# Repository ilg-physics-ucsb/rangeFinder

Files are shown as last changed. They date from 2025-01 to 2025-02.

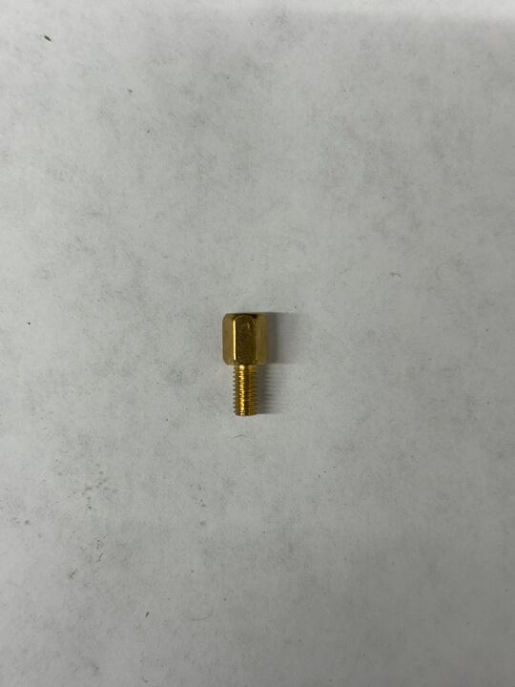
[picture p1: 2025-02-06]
Documentation/Components/M3x6mm_Standoff.jpg

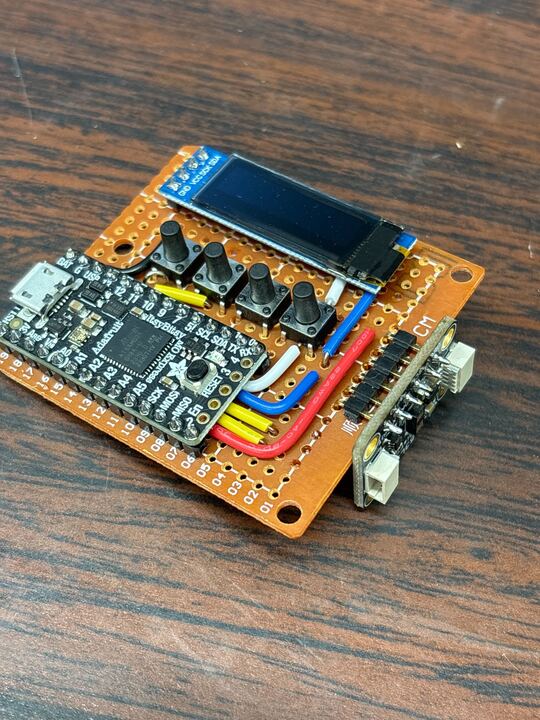
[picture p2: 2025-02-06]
Documentation/CircuitInstructions/CircuitFinished.jpg

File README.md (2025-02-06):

# Range Finder

This repository should hold everything related to the range finders made by the ILG for the 6AL lab series. These range finders were made using off the shelf components from adafruit and amazon with a 3D printed case, to solve the issue of tedious data taking in the Energy Conservation lab in 6AL. For information on the components visit the datasheets folder, for information on the housing view the CAD folder, and to view the code view the code folder. 

## Assembly Instructions

#### Materials required

* 1 [Adafruit ItsyBitsy M0](/Documentation//Components/ItsyBitsyM0ExpressGuide.pdf)
* 1 [Adafruit VL53L1X Breakout Board](/Documentation/Components/VL53L1XGuide.pdf)
* 1 [128x32 I2C SSD1306 OLED Display](/Documentation/Components/SSD1306OLEDGuide.pdf)
* 4 [6x6mm Tall Buttons with Colored Caps](/Documentation/Components/6mmx6mm_Button_Tall.jpg)
* 1 [5cm x 7cm Perf Board](/Documentation/Components/5cmx7cm_PerfBoard.jpg)
* 3 M3x6mm Screws
* 3 [M3x6mm Standoffs](/Documentation/Components/M3x6mm_Standoff.jpg)
* 3 [M3x6mm Threaded Inserts](/Documentation/Components/M3x6mm_ThreadedInsert.jpg)
* 2 [M4 Threaded Banana Plugs](/Documentation/Components/M4_BananaPlug.jpg)
* 2 [M4x8mm Threaded Inserts](/Documentation/Components/M4x8mm_ThreadedInsert.jpg)

#### Assembling the Internals

The Perf board must be cut fairly exactly to size for it to fit in the case. 

* First [score and snap](/Documentation/PerfBoardInstructions/ScoredPerfBoard.jpg) the perf board along row 20. 
* Then [sand along the edge](/Documentation/PerfBoardInstructions/SandedPerfBoard.jpg) to make smooth. 
* Lastly to attach you need [M3 clearance holes drilled](/Documentation/PerfBoardInstructions/FinishedPerfBoard.jpg) into the two holes at the bottom and into the hole at J18. 

From here you can solder all the connections together on the perf board. The schematic used is [shown here](/Documentation/CircuitInstructions/RangeFinderSchematic.pdf). The connections are tight so here are pictures of the asiest way to solder all the connections together: [Top of Circuit](/Documentation/CircuitInstructions/CircuitTop.jpg), [Bottom of Circuit](/Documentation/CircuitInstructions/CircuitBottom.jpg), and a [Finished Circuit](/Documentation/CircuitInstructions/CircuitFinished.jpg). The solder joints must be carefully checked, the ItsyBitsy has a tendency to shut down the I2C lines if there is too much noise on SCL or SDA causing the system to no longer work. If the circuit is not working you should first check that all connectons made are correct according to the scematic, and then if it still is failing ensure that all the solder joints are clean and nothing is even close to touching the SCL or SDA lines. 

#### Assembling the Case

The files for the case can be found [here](/CAD/). This folder contains the raw [Fusion 360 file](/CAD/RangeFinderCase.f3d) if it needs to be edited in the future, as well as .stl files for the [lid](/CAD/RangeFinderLid.stl) and the [main body](/CAD/RangeFinderBody.stl), for easier printing. Once the files are printed you need to [install the threaded inserts](Documentation/CaseInstructions/InstallThreadedInserts.jpg) into the holes. The 3 M3x6mm threaded inserts go in the [main cavity of the body](Documentation/CaseInstructions/M3InsertLocation.jpg) and the 2 M4x8mm threaded inserts go in the [bottom channel](Documentation/CaseInstructions/M4InsertLocation.jpg). 

From here you just put everything together. First you [screw in the M4 Banana Plugs](Documentation/CaseInstructions/M4BananaPlugInsert.jpg) to interface with the air track. Next you [screw the main circuit in](Documentation/CaseInstructions/CircuitInCase.jpg) to the case with the M3x6mm Standoffs. The last step is to just [screw on the lid](Documentation/CaseInstructions/FinalCase.jpg) with the M3x6mm screw. 

#### Flashing the Code

The code for this system was made in Arduino IDE and requires the built in libraries to fuction properly, so to flash the code you must use this IDE. The raw .ino file can be found [here](/Code/RangeFinderCode/). To properly compile the code you will also need to install the core for the ItsyBitsy through Arduino IDE, to do this you will need to follow the steps in the ItsyBitsy datasheet. The code also requires a few libraries to work, you can find all of these [here](/Code/Libraries/). You will need copy these over into the libraries sub-folder of wherever the Aduino IDE stores its files, often in "~/documents/Arduino/". From here you should be able to compile and upload the code to the ItsyBitsy when it is plugged into your computer.

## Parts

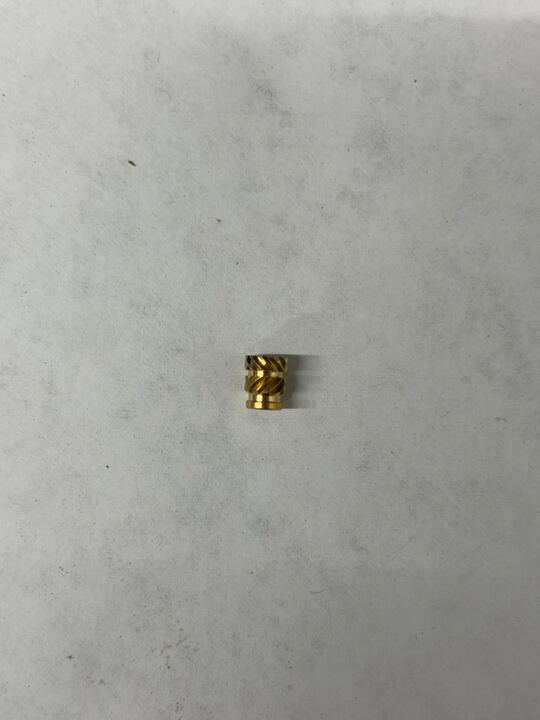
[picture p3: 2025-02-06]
Documentation/Components/M3x6mm_ThreadedInsert.jpg

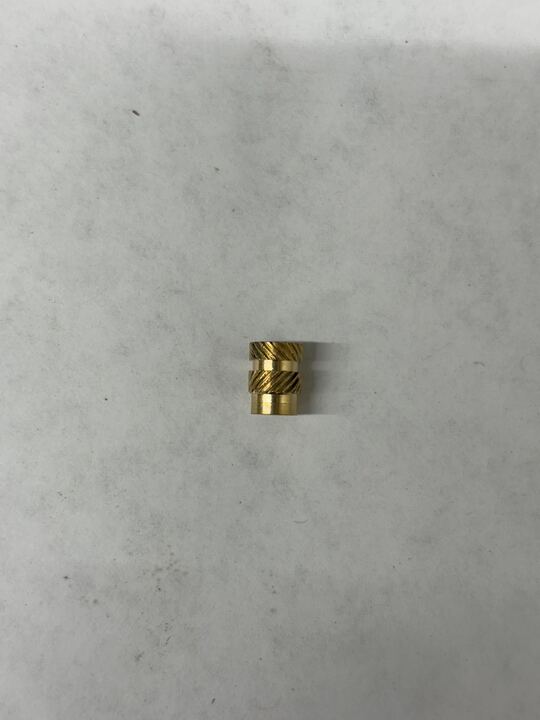
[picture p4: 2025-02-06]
Documentation/Components/M4x8mm_ThreadedInsert.jpg

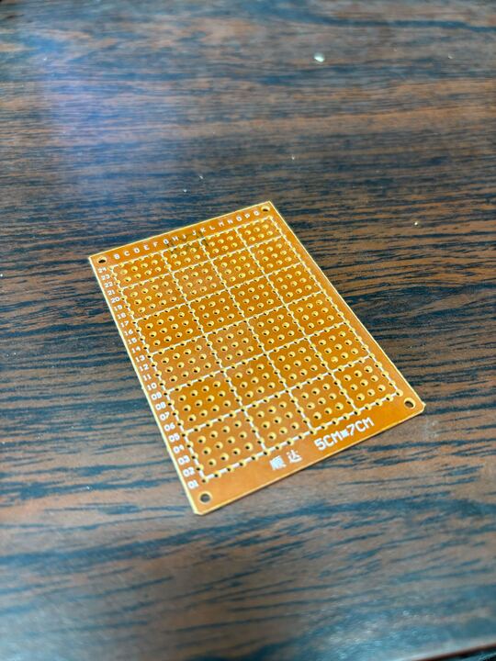
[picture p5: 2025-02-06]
Documentation/Components/5cmx7cm_PerfBoard.jpg

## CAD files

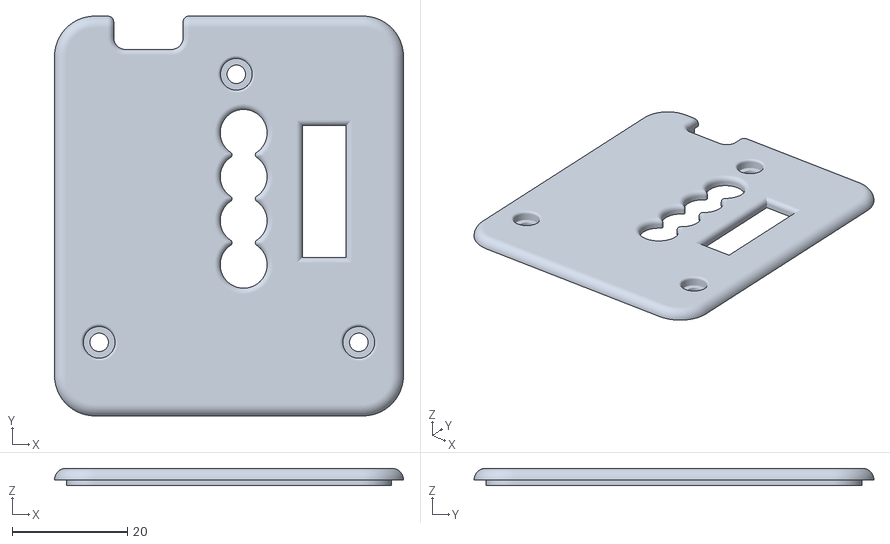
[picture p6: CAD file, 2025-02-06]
CAD/RangeFinderLid.stl
60.5 x 69.3 x 3.00

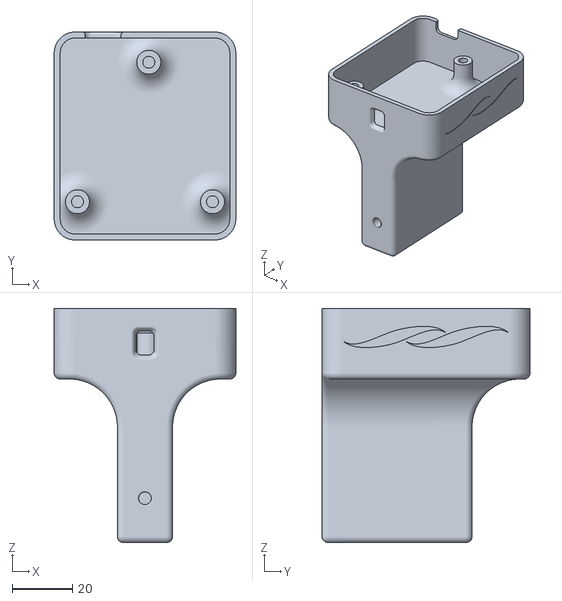
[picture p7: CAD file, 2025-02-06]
CAD/RangeFinderBody.stl
60.5 x 69.3 x 77.9

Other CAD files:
CAD/RangeFinderCase.f3d

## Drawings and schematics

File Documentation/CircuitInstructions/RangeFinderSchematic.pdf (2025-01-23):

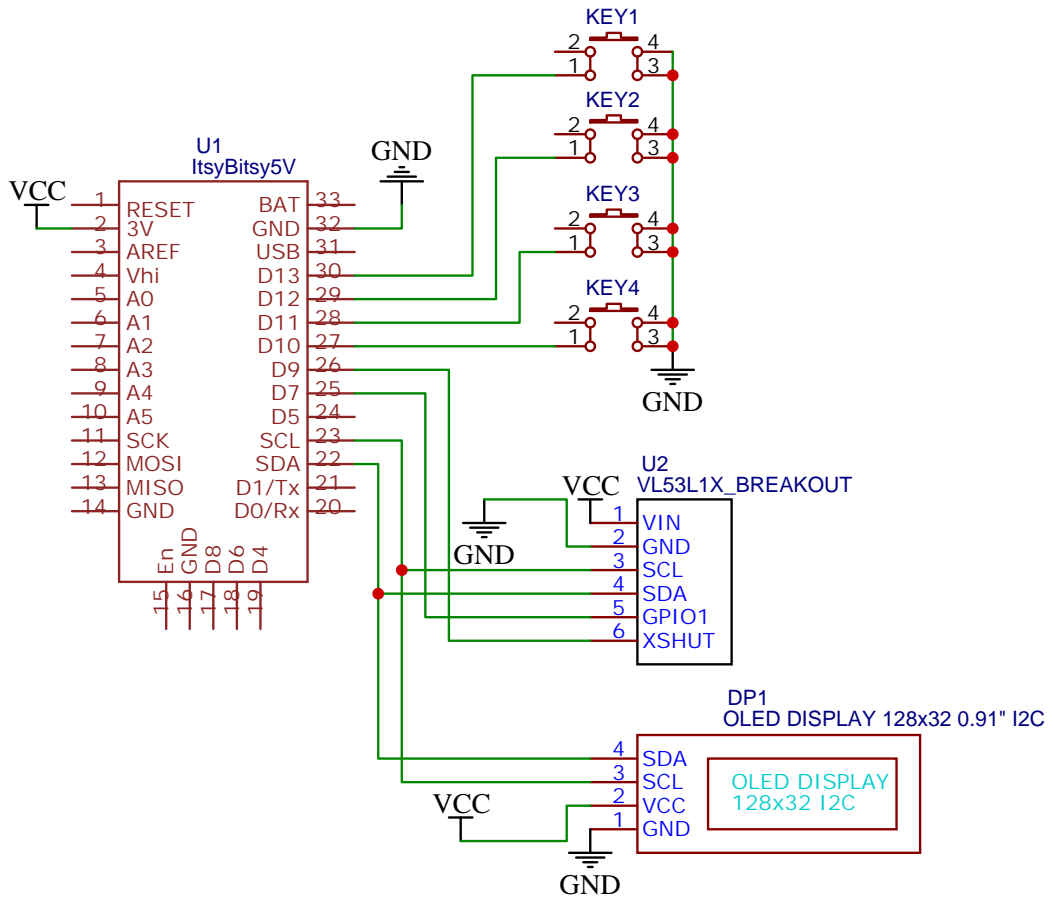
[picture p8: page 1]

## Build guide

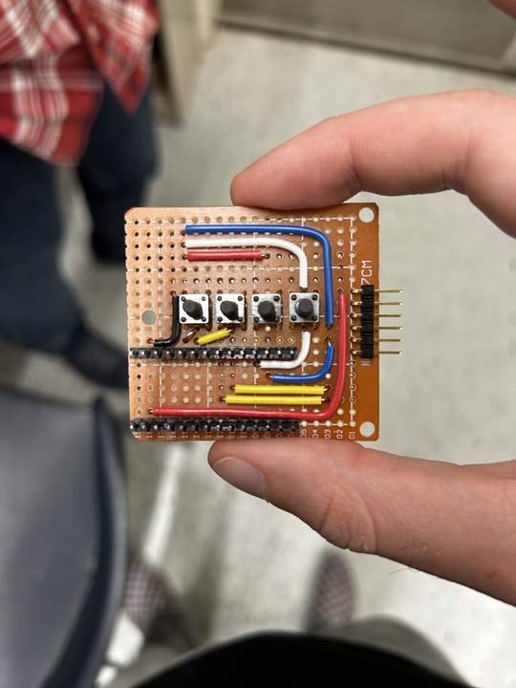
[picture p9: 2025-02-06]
Documentation/CircuitInstructions/CircuitTop.jpg

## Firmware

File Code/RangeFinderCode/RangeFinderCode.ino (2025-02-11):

#include <Adafruit_GFX.h>
#include <Adafruit_SSD1306.h>
#include <vl53l1x_class.h>
#include <Keyboard.h>
#include <Adafruit_DotStar.h>

#define SCREEN_WIDTH 128 // OLED display width, in pixels
#define SCREEN_HEIGHT 32 // OLED display height, in pixels
#define OLED_RESET     -1 // Reset pin # (or -1 if sharing Arduino reset pin)
#define SCREEN_ADDRESS 0x3C // See datasheet for Address; 0x3D for 128x64, 0x3C for 128x32

#define PIN_INDICATOR 2   // Light up LED
#define PIN_START 10      // Green Button
#define PIN_STOP 13       // Red Button
#define PIN_TIME 11       // Blue Button
#define PIN_RATE 12       // Yellow Button
#define PIN_INTERRUPT 7   // Interrupt for the Range Finder
#define PIN_SHUTDOWN 9    // Shutdown pin for the Range Finder

#define DATA_AVG_MAX 10   // How manyt samples for the rolling average

Adafruit_SSD1306 display(SCREEN_WIDTH, SCREEN_HEIGHT, &Wire, OLED_RESET);
VL53L1X rangeFinder(&Wire, PIN_SHUTDOWN);
Adafruit_DotStar onBoardLED(DOTSTAR_NUM, PIN_DOTSTAR_DATA, PIN_DOTSTAR_CLK, DOTSTAR_BRG);

uint8_t dataFlag = 0 ;
int dataStatus = 0 ;
int objectNum = 0 ;
int dataRawTime = 50 ; // Time for the sensor to average over 
uint16_t dataRaw = 0 ;
float data = 0 ;
int dataAvg[DATA_AVG_MAX] ;
unsigned long dataTime[DATA_AVG_MAX] ;
int dataAvgIndex = 0 ;

int dataRecordingIntervalIndex = 4 ;
unsigned long dataRecordingInterval[] = {10000, 15000, 20000, 30000, 5000} ; // How long to record data in millis
int dataRecordingIntervalSize = 5 ;                                          // Number of entries in the array above
unsigned long dataRecordingTimeStart = 0 ;
char dataRecordingIntervalBuff[5] ;
int dataRecordingIntervalPos[2][2] = { {94, 24}, {30, 0} } ;


int dataFilterIntervalIndex = 0 ;
unsigned long dataFilterInterval[] = {1, 2, 5, 10, 20};              // Time for the us to filter the sensors data over as number of samples
int dataFilterIntervalSize = 5 ;                                             // Number of entries in the array above
unsigned long dataFilterTime = 0 ;    
char dataFilterIntervalBuff[5] ;   
int dataFilterIntervalPos[2][2] = { {30, 24}, {94, 0} } ;

// legacy variables for filtering
float dataLast = 0 ;
float dataLastLast = 0 ;
float timeLast = 0 ;     // Last time for velocity
float timeLastLast = 0 ; // Last Last time for velocity
float posLast = 0 ;         // Last position for filtering
float velLast = 0 ;         // Last velocity for filtering
float alpha = 0.5 ;        // Factor for data smoothing 
float alphaInv = 1-alpha ;  // Precalculating 

// Data to be stored and written to computer
float time = 0 ;         // Time of recorded data
float pos = 0 ;             // Smoothed data in m
float vel = 0 ;             // Smoothed data of velocity in m/s
char posBuff[5] ;
char velBuff[6] ;
char timeBuff[6] ;

bool dataNewFlag = 0 ;
int dataArrayIndex = 0 ;
int dataArrayCounter = 0 ;
int dataArrayCounterSub = 0 ;
float timeArray[1000] ;
float posArray[1000] ;
float velArray[1000] ;
unsigned long keyboardDelay = 50 ;
unsigned long keyboardTimer = 0 ;


int posPixelX = 0 ;
int posPixelY = 0 ;
int displayRotation = 0 ;
int dataDistancePos[2][2] = { {22, 0}, {22, 16} } ;
int dataUploadPos[2][2] = { {89, 0}, {3, 0} }  ;
int dataCancelPos[2][2] = { {3, 0}, {89, 0} }  ;

unsigned long displayInterval = 200 ;
unsigned long displayTime = 0 ;

unsigned long buttonDebounceWait   = 20 ;  // In millis
unsigned long buttonStartDebounce  = 0 ;
unsigned long buttonStopDebounce   = 0 ;
unsigned long buttonRateDebounce   = 0 ;
unsigned long buttonTimeDebounce   = 0 ;
bool buttonStartToggle    = 0 ;
bool buttonStopToggle     = 0 ;
bool buttonRateToggle     = 0 ;
bool buttonTimeToggle     = 0 ;
bool buttonStartFlag      = 0 ;
bool buttonStopFlag       = 0 ;
bool buttonRateFlag       = 0 ;
bool buttonTimeFlag       = 0 ;

int state = 0 ;
int stateLast = 0 ;
bool displayFlag = 0 ;
volatile bool interruptFlag = 0;
unsigned long t0 = 0 ;


void interruptRangeFinder() {
  interruptFlag = 1;
}


// the setup function runs once when you press reset or power the board
void setup() {
  // Init on Board LED
  onBoardLED.begin(); // Initialize pins for output
  onBoardLED.setBrightness(80);
  onBoardLED.show();  // Turn all LEDs off ASAP


  // initialize GPIO pins
  pinMode(PIN_START, INPUT_PULLUP) ;
  pinMode(PIN_STOP,  INPUT_PULLUP) ;
  pinMode(PIN_TIME,  INPUT_PULLUP) ;
  pinMode(PIN_RATE,  INPUT_PULLUP) ;
  pinMode(PIN_INDICATOR,   OUTPUT) ;
  pinMode(PIN_INTERRUPT, INPUT_PULLUP);
  attachInterrupt(PIN_INTERRUPT, interruptRangeFinder, RISING) ;

  // Start up the rangefinder in interrupt mode
  Serial.println("Init Range Finder") ;
  onBoardLED.setPixelColor(0, 0, 255, 0) ; // Show the program through the LEDs
  onBoardLED.show();
  Wire.begin() ;
  rangeFinder.begin();
  rangeFinder.VL53L1X_Off();
  rangeFinder.InitSensor(0x29) ;
  rangeFinder.VL53L1X_SetROI(4, 4) ;
  rangeFinder.VL53L1X_SetDistanceMode(2) ; // Medium Distance Mode
  rangeFinder.VL53L1X_SetTimingBudgetInMs(dataRawTime) ;
  rangeFinder.VL53L1X_SetInterMeasurementInMs(dataRawTime) ;
  rangeFinder.VL53L1X_StartRanging() ;
  onBoardLED.setPixelColor(0, 0, 0, 0) ; // Show the program through the LEDs
  onBoardLED.show();

  // Start up display
  onBoardLED.setPixelColor(0, 0, 0, 255) ; // Show the program through the LEDs
  onBoardLED.show();
  display.begin(SSD1306_SWITCHCAPVCC, SCREEN_ADDRESS) ;
  display.setTextSize(1) ;                             // Normal 1:1 pixel scale
  display.setTextColor(SSD1306_WHITE, SSD1306_BLACK) ; // Draw white text
  if (displayRotation == 0){
    display.setRotation(0) ;
  } else {
    display.setRotation(2) ;
  }
  initDisplay(state) ;
  onBoardLED.setPixelColor(0, 0, 0, 0) ; // Show the program through the LEDs
  onBoardLED.show();

  //Initialize Keyboard
  Keyboard.begin() ;
}

void loop() {
  // Update interactives
  updateButtons() ;
  updateRangeFinder() ;

  // Main state machine for handling data
  stateLast = state ;
  switch(state) {
    case 0:
      // Idle mode: Display distance and react to buttons

      // Update position so you know the sensor is working
      if (millis() - displayTime >= displayInterval){
        displayTime = millis() ;
        display.setTextSize(2) ;
        display.setCursor(dataDistancePos[displayRotation][0], dataDistancePos[displayRotation][1]) ;
        formatPos((float)dataAvg[ mod(dataAvgIndex-1, DATA_AVG_MAX) ]/1000) ;
        display.print(posBuff) ;
        display.print("m") ;
        display.setTextSize(1) ;
        displayFlag = 1 ;

      } 

      // Start recording data is green button pressed
      if (buttonStartFlag){
        state = 1 ;
        initDisplay(state) ;
        dataRecordingTimeStart = millis() ;
      }

      // Adjust the length of data collection
      if (buttonTimeFlag){
        buttonTimeFlag = 0 ;
        dataRecordingIntervalIndex = (dataRecordingIntervalIndex+1)%dataRecordingIntervalSize ;
        formatRecordingInterval() ;
        display.setCursor(dataRecordingIntervalPos[displayRotation][0], dataRecordingIntervalPos[displayRotation][1]) ;
        display.print(dataRecordingIntervalBuff) ;
        displayFlag = 1 ;
      }

      // Adjusts the rate at which data is taken
      if (buttonRateFlag){
        buttonRateFlag = 0 ;
        dataFilterIntervalIndex = (dataFilterIntervalIndex+1)%dataFilterIntervalSize ;
        formatFilterInterval() ;
        display.setCursor(dataFilterIntervalPos[displayRotation][0], dataFilterIntervalPos[displayRotation][1]) ;
        display.print(dataFilterIntervalBuff) ;
        displayFlag = 1 ;
      }

      // Rotate the display if needed
      if (buttonStopFlag){
        buttonStopFlag = 0 ;
        displayRotation = (displayRotation+1) % 2 ;
        if (displayRotation == 0){
          display.setRotation(0) ;
        } else {
          display.setRotation(2) ;
        }
        initDisplay(state) ;
      }

      // Need to handle data New flag even if not used
      if (dataNewFlag){
        dataNewFlag = 0 ;
      }
    break;
    case 1:
      // Recording mode: Display graph of distance and only react to red button

      if (dataNewFlag){
        dataNewFlag = 0 ;
        // If new data available record it
        // Records all data, can be parsed for sparser data when recorded
        timeArray[dataArrayIndex] = time ;
        posArray[dataArrayIndex] = pos ;
        velArray[dataArrayIndex] = vel ;
        dataArrayIndex ++ ;

        posPixelX = 128*time*1000/dataRecordingInterval[dataRecordingIntervalIndex] ;  // Divided by max time on graph
        posPixelY = 31 - 32*pos/2 ;                                               // Divided by max position showable

        display.drawPixel(posPixelX, posPixelY, SSD1306_WHITE) ;
        displayFlag = 1 ;

      }


      // End data recording and write is all to the keyboard if its time
      if (millis() - dataRecordingTimeStart >= dataRecordingInterval[dataRecordingIntervalIndex]){
        state = 2 ;
        initDisplay(state) ;
      }

      // Also end recording if red button pressed
      if (buttonStopFlag){
        buttonStopFlag = 0 ;
        state = 0 ;
        initDisplay(state) ;
        dataArrayIndex = 0 ;
        dataArrayCounter = 0 ;
        dataArrayCounterSub = 0 ;
      }

      // Need to handle buttons even if not used
      if (buttonStartFlag){
        buttonStartFlag = 0 ;
      }
      if (buttonRateFlag){
        buttonRateFlag = 0 ;
      }
      if (buttonTimeFlag){
        buttonTimeFlag = 0 ;
      }
    break;
    case 2:
      // Wait for user input to actually upload the data to your computer

      // Start writing data if not canceled
      if (buttonStartFlag){
        buttonStartFlag = 0 ;
        state = 3 ;
        initDisplay(state) ;
      }
      // Do not record if canceled
      if (buttonStopFlag){
        buttonStopFlag = 0 ;
        state = 0 ;
        initDisplay(state) ;
        dataArrayIndex = 0 ;
        dataArrayCounter = 0 ;
        dataArrayCounterSub = 0 ;
      }

      // Need to handle buttons even if not used
      if (buttonRateFlag){
        buttonRateFlag = 0 ;
      }
      if (buttonTimeFlag){
        buttonTimeFlag = 0 ;
      }

      // Need to handle data New flag even if not used
      if (dataNewFlag){
        dataNewFlag = 0 ;
      }
    break;
    case 3:
      // Write mode: Triggered on end of recording mode, to write data to keyboard


      // Only write to the keyboard after a specified keyboard delay each loop
      if (millis() - keyboardTimer >= keyboardDelay){
        keyboardTimer = millis() ;

        // each data entry takes multiple delays, so cycle through with switch case
        switch(dataArrayCounterSub){
          case 0:
            Keyboard.release('\n') ;
            Keyboard.print(timeArray[dataArrayCounter], 4) ;
          break;
          case 1:
            Keyboard.press('\t') ;
          break;
          case 2:
            Keyboard.release('\t') ;
            Keyboard.print(posArray[dataArrayCounter], 4) ;
          break;
          case 3:
            Keyboard.press('\t') ;
          break;
          case 4:
            Keyboard.release('\t') ;
            Keyboard.print(velArray[dataArrayCounter], 4) ;
          break;
          case 5:
            Keyboard.press('\n') ;
          break;
        }

        // Increment the Subcounter and if overflows, increment which data to write
        dataArrayCounterSub ++ ;
        if (dataArrayCounterSub > 5){
          dataArrayCounterSub = 0 ;
          dataArrayCounter += dataFilterInterval[dataFilterIntervalIndex] ;
        }

      }
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

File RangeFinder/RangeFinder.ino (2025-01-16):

#include <Arduino.h>
#include <Wire.h>
#include <Adafruit_GFX.h>
#include <Adafruit_SSD1306.h>
#include <vl53l4cx_class.h>
#include <string.h>
#include <stdlib.h>
#include <stdio.h>
#include <stdint.h>
#include <assert.h>
#include <stdlib.h>
#include <Keyboard.h>

#define SCREEN_WIDTH 128 // OLED display width, in pixels
#define SCREEN_HEIGHT 32 // OLED display height, in pixels
#define OLED_RESET     -1 // Reset pin # (or -1 if sharing Arduino reset pin)
#define SCREEN_ADDRESS 0x3C // See datasheet for Address; 0x3D for 128x64, 0x3C for 128x32

#define PIN_START 10      // Green Button
#define PIN_STOP 13       // Red Button
#define PIN_TIME 11       // Blue Button
#define PIN_RATE 12       // Yellow Button
#define PIN_INTERRUPT 7   // Interrupt for the Range Finder

Adafruit_SSD1306 display(SCREEN_WIDTH, SCREEN_HEIGHT, &Wire, OLED_RESET);
VL53L4CX rangeFinder(&Wire, 9);

VL53L4CX_MultiRangingData_t rangeFinderData;
VL53L4CX_MultiRangingData_t *pRangeFinderData = &rangeFinderData;
uint8_t dataFlag = 0 ;
int dataStatus = 0 ;
int objectNum = 0 ;
unsigned long dataRawTime = 50 ; // Time for the sensor to average over 
int dataRaw = 0 ;

int dataRecordingIntervalIndex = 0 ;
unsigned long dataRecordingInterval[] = {10000, 15000, 20000, 30000, 5000} ; //How long to record data in millis
unsigned long dataRecordingTime = 0 ;
char dataRecordingIntervalBuff[5] ;


int dataFilterIntervalIndex = 0 ;
unsigned long dataFilterInterval[] = {200, 500, 1000, 50, 100};              // Time for the us to filter the sensors data over
unsigned long dataFilterTime = 0 ;    
int dataFilterSamples = dataFilterInterval[dataFilterIntervalIndex]/dataRawTime ;
char dataFilterIntervalBuff[5] ;                          

float time = 0 ;            // Time of recorded data
unsigned long timeAbs = 0 ; // counter to get absolute time difference
float pos = 0 ;             // Smoothed data in m
float posLast = 0 ;         // Last position for velocity calculation
float vel = 0 ;             // Smoothed data of velocity in m/s
float alpha = 0.95 ;        // Factor for data smoothing 
float alphaInv = 1-alpha ;  // Precalculating 
char posBuff[5] ;
char velBuff[8] ;
char timeBuff[6] ;

bool dataNewFlag = 0 ;
int dataArrayIndex = 0 ;
float timeArray[1000] ;
float posArray[1000] ;
float velArray[1000] ;
int keyboardDelay = 40 ;

int posPixelX = 0 ;
int posPixelY = 0 ;

unsigned long displayInterval = 200 ;
unsigned long displayTime = 0 ;

unsigned long buttonDebounceWait   = 20 ;  // In millis
unsigned long buttonStartDebounce  = 0 ;
unsigned long buttonStopDebounce   = 0 ;
unsigned long buttonRateDebounce   = 0 ;
unsigned long buttonTimeDebounce   = 0 ;
bool buttonStartToggle    = 0 ;
bool buttonStopToggle     = 0 ;
bool buttonRateToggle     = 0 ;
bool buttonTimeToggle     = 0 ;
bool buttonStartFlag      = 0 ;
bool buttonStopFlag       = 0 ;
bool buttonRateFlag       = 0 ;
bool buttonTimeFlag       = 0 ;

int state = 0 ;
int stateLast = 0 ;
bool displayFlag = 0 ;
volatile bool interruptFlag = 0;
unsigned long t0 = 0 ;


void interruptRangeFinder() {
  interruptFlag = 1;
}
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

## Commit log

2024-12-11 Add Testing arduino code
2025-01-17 Fix filter and try new sensor
2025-01-21 Testing new sensor
2025-02-04 Start new filtering system
2025-02-06 Reorganized Source code
    [RangeFinderBody.stl, RangeFinderCase.f3d, RangeFinderLid.stl]
2025-02-06 Add Assembly Instructions
